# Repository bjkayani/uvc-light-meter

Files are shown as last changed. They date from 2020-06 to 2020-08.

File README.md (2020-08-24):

# UV-C Light Meter
Low Cost UV-C Light Meter with Dual Sensor Input and Data Logging

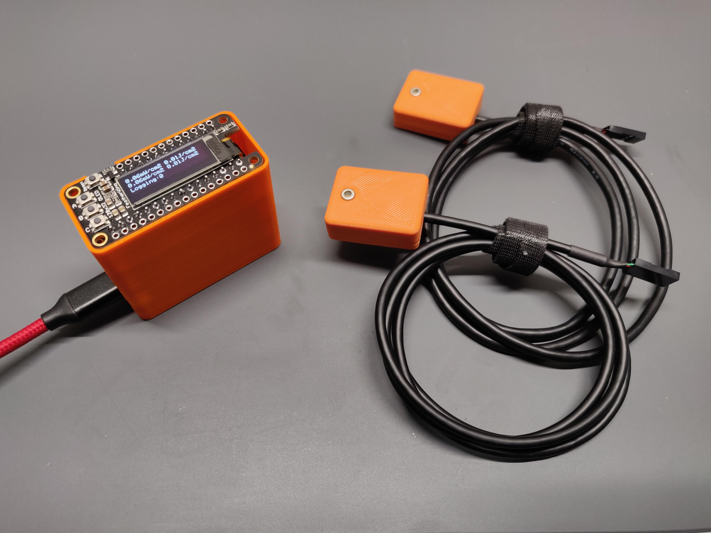
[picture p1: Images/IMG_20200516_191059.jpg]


## Background
UV-C based devices are being widely developed on comercial and hobby levels in response to COVID-19. As a result,
there is a shortage of testing equipment including UV-C meters. Hence I developed this low cost solution that can 
be used to measure UV-C intesity. 

## Features
The meter features a small and compact form factor with an oled display. It has a built in RTC and SD card to log
time stamped measurements. It can be used with upto two sensors and further sensors can be added with some modification. 

## Bill of Materials
**Note:** I used the Adafruit Feather ecosystem of development boards for this project for their ease of use and quick assembly. But this meter can
be made using a wide variety of parts so feel free to go for a cheaper option. 
| Part Name | Manufacturer Part Number | Description | Digikey Link |
| ----------- | ----------- | ----------- | ----------- |
| Genicom UV-C Sensor | GUVC-T10GM-LA | This is the sensor used to measure UV-C intesity. It comes precalibrated on a small PCB with an opamp to give a linear analog output.| [GUVC-T10GM-LA](https://www.digikey.com/product-detail/en/genicom-co-ltd/GUVC-T10GM-LA/2096-GUVC-T10GM-LA-ND/10474940) |
| Adafruit Feather M4 Express | 3857 | I used the Feather M4 for its 10bit ADC but you can use any Feather you want. | [Adafruit Feather M4 Express](https://www.digikey.com/product-detail/en/adafruit-industries-llc/3857/1528-2648-ND/9553567)|
| Adalogger Featherwing - RTC + SD | 2922 | The featherwing that adds RTC and SD card functionality. | [Adalogger Featherwing - RTC + SD](https://www.digikey.com/product-detail/en/adafruit-industries-llc/2922/1528-1621-ND/5885911) |
| Featherwing OLED Display | 2900 | The featherwing that displays the current readout and allows for control through buttons. | [Featherwing OLED Display](https://www.digikey.com/product-detail/en/adafruit-industries-llc/2900/1528-1547-ND/5810890) |
| Featherwing Proto | 2884 | Featherwing used to construct the simple circuit | [Featherwing Proto](https://www.digikey.com/product-detail/en/adafruit-industries-llc/2884/1528-1622-ND/5777193) |
| Featherwing Stacking Headers | 2830 | Used to stack all featherwings | [Featherwing Stacking Headers](https://www.digikey.com/product-detail/en/adafruit-industries-llc/2830/2830-ND/5823439) |
| Coin Cell CR1220 | CR1220 | Battery for the data logger | [Coin Cell CR1220](https://www.digikey.com/product-detail/en/panasonic-bsg/CR1220/P033-ND/269740) |
| Dual Right-Angle Male Pin Header Strip | 1541 | Used for sensor connection to the protoboard | [Dual Right-Angle Male Pin Header Strip](https://www.adafruit.com/product/1541) |
| 2.2K Resistor | 2782 | Used to make the voltage divider | [2.2k Resistor](https://www.adafruit.com/product/2782) |
| 1.0K Resistor | 4294 | Used to make the voltage divider | [1.0k Resistor](https://www.adafruit.com/product/4294) |

## Build Guide
The build is pretty straight forward. If you have a little bit of experience making things, you would be able to figure it out without this guide. 

### Assembly

- The first step is to prepare all your materials and for that, you would need to 3D print the parts located in the Hardware section of the repo. Use 100% infill and a fine layer height for high quality printing. 
- Next, you will solder the stackable headers on the featherwing proto and featherwing datalogger. You will solder male headers on the featherwing oled and female headers on the feather M4 express. 
- You will make a simple voltage divider circuit and solder angled pin headers for the UV-V sensors. The snesors work with 5V so you need to decrease their output so that it doesnt exceed the 3.3V thershold. 
- You will prepare the sensor by desoldering the connector that it comes with and soldering wires to the +5V, GND and Data pins. I used an old USB cable for this but you could also use some other thin and felxible wires. I crimped a 3p dupont connector on the other end. 
- Secure the sensor in the 3D printed case and add some glue to hold the wire in place. I used E6000 and then closed the cover. 
- Screw in the M4 express in the base of the case and then stack on the datalogger wing followed by the proto wing and finally the oled wing.
- Your meter should now be ready for programming. 

### Programming
I used platformIO on VSCode for this project and the code provided is a platformIO project. You would need to install Visual Studio Code followed by the PlatformIO extension. Within the extension, you can open my project and upload it to your feather. If you run into any issue, there is plenty of documentation online on how to get start with PIO and the community is very helpful. 

You can also use the same code to upload through the Arduino IDE but it would require installation of the board and all the required libraries so you are on your own for that. 

### Calibration

Calibration shouldnt be needed in most cases given the same sensor is used. But if you do need to calibrate the device, you will change the MULT_A and MULT_B to 1. Then you will measure UV-C from a source and record your meter reading and the actual reading from an off the shelf meter. Take a few measurements at different distances from the source. Then use some math to calculate the constant needed for each of measurements and get the average of the constants for a final multiplier. 

## Contact Information
If you want more information regarding this project, please contact me via email at badarjahangir@gmail.com

## Acknowledgements
The support for this project was provided generously by the donors of Sears think[box] at Case Western Reserve University.

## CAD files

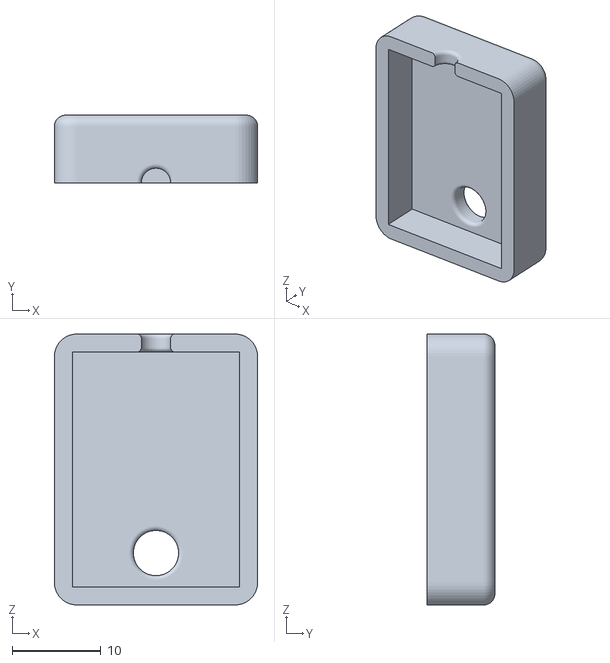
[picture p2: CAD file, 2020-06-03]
Hardware/3D Print Files/Sensor Box Base.STL
22.9 x 7.62 x 30.5

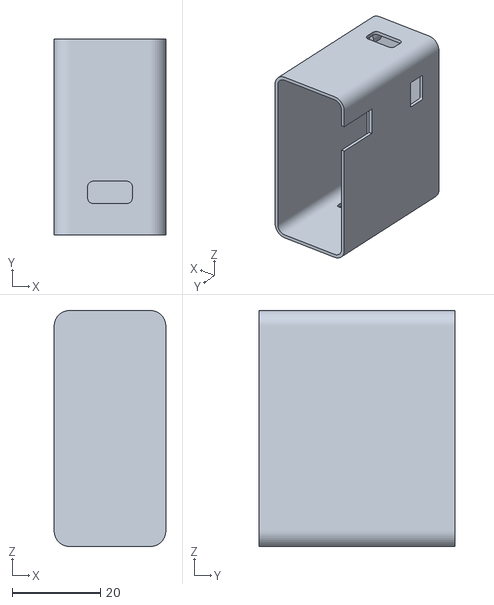
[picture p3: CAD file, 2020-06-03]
Hardware/3D Print Files/Meter Casing.STL
25.4 x 44.5 x 53.6

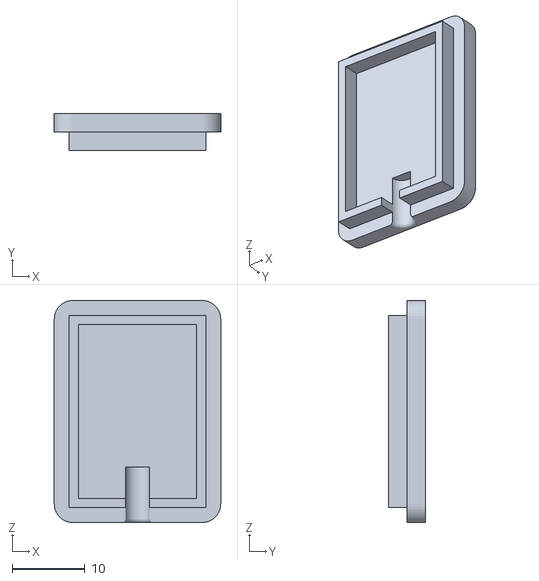
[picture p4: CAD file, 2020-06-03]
Hardware/3D Print Files/Sensor Box Top.STL
22.9 x 5.08 x 30.5
